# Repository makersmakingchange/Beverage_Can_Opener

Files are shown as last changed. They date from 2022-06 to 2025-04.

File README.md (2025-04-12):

# Beverage Can Opener
A tool to open beverage cans with a simple hook and lever motion.

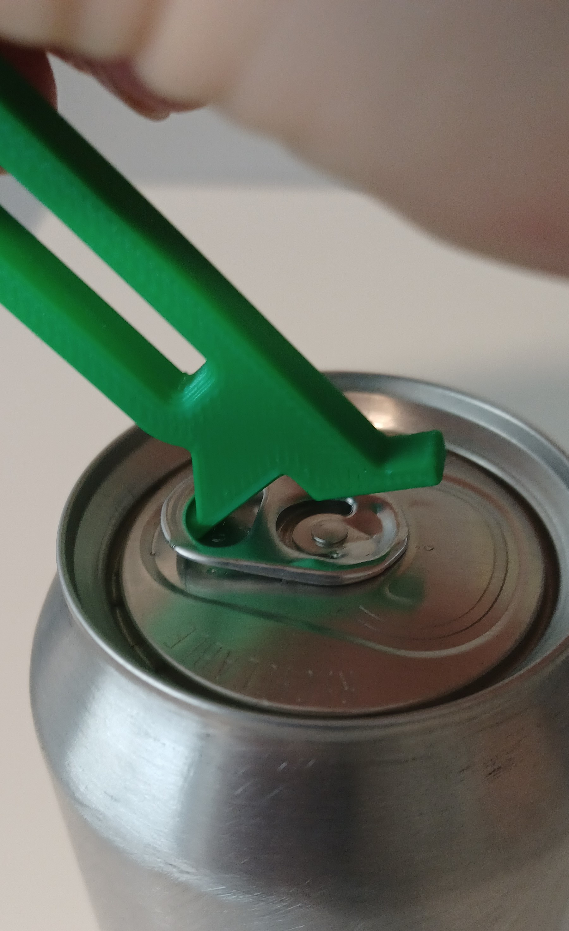
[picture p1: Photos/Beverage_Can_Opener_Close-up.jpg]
Picture of Printlab Can Opener.


## More info at
- [Makers Making Change Project Page](https://makersmakingchange.com/project/beverage-can-opener-from-printlab/)

## How to Obtain a Beverage Can Opener
### 1. Do it Yourself (DIY) or Do it Together (DIT)

This is an open-source assistive technology, so anyone is free to build it. All of the files and instructions required to build the Beverage Can Opener are contained within this repository. Refer to the Maker Checklist below.

### 2. Request a build of this device

If you would like to obtain a Beverage Can Opener, you may submit a build request through the [MMC Library Page](https://makersmakingchange.com/project/beverage-can-opener/). The requestor is responsible for the cost of materials and any shipping.

### 3. How to build this device for someone else

If you have the skills and equipment to build this device, and would like to donate your time to create the switch for someone who needs it, visit the [MMC Maker Wanted](https://makersmakingchange.com/maker-wanted/) section.

## Getting Started

### 1. Read the [Makers Checklist](/Documentation/Beverage_Can_Opener_Maker_Checklist_V1.0.pdf)

### 2. Print the Device

All of the print files can be in the [/Build_Files/3D_Print_Files](/Build_Files/3D_Print_Files/) folder.

Detailed instructions about 3D Printing settings can be found in the [3D Printing Guide](/Documentation/Beverage_Can_Opener_3D_Printing_Guide_V1.0.pdf).

## Files
### Documentation
| Document             | Version | Link |
|----------------------|---------|------|
| Design Rationale     | 1.0     | [Beverage_Can_Opener_Design_Rationale](/Documentation/Beverage_Can_Opener_Design_Rationale_V1.0.pdf)     |
| Maker Checklist      | 1.0     | [Beverage_Can_Opener_Maker_Checklist](/Documentation/Beverage_Can_Opener_Maker_Checklist_V1.0.pdf)     |
| Bill of Materials    | 1.0     | [Beverage_Can_Opener_Bill_of_Materials](/Documentation/Beverage_Can_Opener_BOM_V1.0.csv)     |
| 3D Printing Guide    | 1.0     | [Beverage_Can_Opener_3D_Printing_Guide](/Documentation/Beverage_Can_Opener_3D_Printing_Guide_V1.0.pdf)     |
| User Guide           | 1.0     | [Beverage_Can_Opener_User_Guide](/Documentation/Beverage_Can_Opener_User_Guide_V1.0.pdf)    |
| Changelog            | 1.0     | [Beverage_Can_Opener_Changelog](/Documentation/Beverage_Can_Opener_Changelog_V1.0.pdf)     |

### Design Files
[CAD Files](/Design_Files)

### Build Files
[3D Printing Files](/Build_Files/3D_Print_Files)

## Attribution
Original design by Jason Yeung.
Minor modifications to design and documentation by Neil Squire / Makers Making Change under the CC-BY-SA 4.0 License.
More information about Printlab can be found on their website: https://weareprintlab.com/  under the CC-BY-SA 4.0 License.

## License
Everything needed or used to design, make, test, or prepare the Beverage Can Opener is licensed under the CERN 2.0 Permissive license <https://ohwr.org/project/cernohl/wikis/Documents/CERN-OHL-version-2> (CERN-OHL-P) . 

<br /><span xmlns:dct="http://purl.org/dc/terms/" property="dct:title"><Device-Name></span> by <a xmlns:cc="http://creativecommons.org/ns#" href="www.makersmakingchange.com" property="cc:attributionName" rel="cc:attributionURL">Neil Squire</a> is licensed under a <a rel="license" href="http://creativecommons.org/licenses/by-sa/4.0/">Creative Commons Attribution-ShareAlike 4.0 International License</a>.

---
<!-- ABOUT MMC START -->
## About Makers Making Change
[Makers Making Change Logo](https://www.makersmakingchange.com/)

Makers Making Change is a program of [Neil Squire](https://www.neilsquire.ca/), a Canadian non-profit that uses technology, knowledge, and passion to empower people with disabilities.

Makers Making Change leverages the capacity of community based Makers, Disability Professionals and Volunteers to develop and deliver affordable Open Source Assistive Technologies.

 - Website: [www.MakersMakingChange.com](https://www.makersmakingchange.com/)
 - GitHub: [makersmakingchange](https://github.com/makersmakingchange)
 - Bluesky: [@makersmakingchange.bsky.social](https://bsky.app/profile/makersmakingchange.bsky.social)
 - Instagram: [@makersmakingchange](https://www.instagram.com/makersmakingchange)
 - Facebook: [makersmakechange](https://www.facebook.com/makersmakechange)
 - LinkedIn: [Neil Squire Society](https://www.linkedin.com/company/neil-squire-society/)
 - Thingiverse: [makersmakingchange](https://www.thingiverse.com/makersmakingchange/about)
 - Printables: [MakersMakingChange](https://www.printables.com/@MakersMakingChange)

### Contact Us
For technical questions, to get involved, or to share your experience we encourage you to [visit our website](https://www.makersmakingchange.com/) or [contact us](https://www.makersmakingchange.com/s/contact).
<!-- ABOUT MMC END -->

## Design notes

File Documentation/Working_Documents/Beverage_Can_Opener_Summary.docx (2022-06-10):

# Title

Beverage Can Opener.

## Subtitle

## A tool to open beverage cans with a simple hook and lever motion.

## Device Specifications

Build Time:

< 1hr

1-4 hr

5-10hr

>10hr

Cost:

$0 - $10

$11 - $25

$26 - $50

$51 - $100

$101 - $250

$250+

Stage: Recently Added

Skills: 3D Printing

Need: Agility / Dexterity

Disability: Mobility/Physical

Difficulty: Beginner

License: Attribution-ShareAlike 4.0 International

Usages: Aids for Daily Living (ADL), Mobility

Designer: Jason Yeung

## Device Details

### Overview

The Beverage Can Opener provides a way for those with arthritis, low finger dexterity, low vision, or other related disabilities to open beverage cans with a pull-tab with little strength or accuracy required.

This design is featured in the Assistive Device Academy from Printlab (https://classroom.weareprintlab.com/p/assistive-device-academy-v2).

### Compatibility

This device is compatible with aluminum beverage cans with pull-tabs.

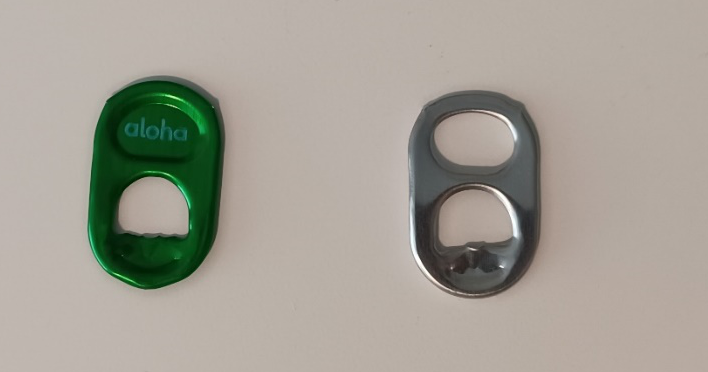
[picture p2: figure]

Some aluminum cans contain a pull-tab with some graphic or logo in the top hole of the tab, as seen in the left of the photo above. Only cans with a tab like the one shown on the right, with a hole in the top of the tab, can be used with this device.

### Similar Devices

- Another device for opening beverage cans, compatible with pull-tabs without a hole in the top (left in photo), is available at https://makersmakingchange.com/project/beverage-can-opener/ (https://makersmakingchange.com/?post_type=project&p=15048&preview=true).
- A device intended for tin food cans with pull-tabs, such as pet food, canned tuna or canned beans, is available at https://makersmakingchange.com/project/pull-tab-tin-can-opener/ (https://makersmakingchange.com/?post_type=project&p=15035&preview=true).

### Cost

Less than $1 CAD.

### Build Instructions

This device consists of a single 3D Printed Part. More comprehensive instructions on 3D Printing this device can be found in the Beverage Can Opener 3D Printing Guide.

#### Design

Full instructions for designing this device using CAD, along with other similar assistive devices, can be found in the Assistive Device Academy from Printlab (https://classroom.weareprintlab.com/p/assistive-device-academy-v2).

#### Skills Required

3D Printing.

#### Time Required

3D printing time: 38 minutes.

#### Tools

3D Printer

### Attribution

Original design by Jason Yeung.

Minor modifications to design and documentation by Neil Squire / Makers Making Change under the CC-BY-SA 4.0 License.

More information about Printlab can be found on their website: https://weareprintlab.com/ under the CC-BY-SA 4.0 License.

© 2022 by Neil Squire / Makers Making Change This work is licensed under the CC BY SA 4.0 License: http://creativecommons.org/licenses/by-sa/4.0 Files available at https://makersmakingchange.com/project/beverage-can-opener/ Page 1 of 2

V1.0 | June 2022 Beverage Can Opener Summary

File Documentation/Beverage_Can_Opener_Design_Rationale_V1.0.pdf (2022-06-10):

V1.0 | June 2022

## Beverage Can Opener

## DESIGN RATIONALE

© 2022 by Neil Squire / Makers Making Change This work is licensed under the CC BY SA 4.0 License: http://creativecommons.org/licenses/by-sa/4.0 Files available at https://makersmakingchange.com/project/beverage-can-opener/ (https://makersmakingchange.com/?post_type=project&p=15019&preview=true)

### Introduction

A device is needed in the Makers Making Change Assistive Device Library which can provide a way for those with arthritis, low finger dexterity, low vision, or other related disabilities open beverage cans with a pull-tab with little strength or accuracy needed.

This device is not intended for tin cans used for storing food, another device for that purpose is provided at https://makersmakingchange.com/project/pull-tab-tin-can-opener/. (https://makersmakingchange.com/?post_type=project&p=15035&preview=true)

### Requirements

### Goals

G01 | To provide a way for those with arthritis or low finger dexterity open the pull-tabs on beverage cans.
G02 | To provide a device cheaper than the commercial option.
G03 | To fit all pull-tabs on beverage cans available in grocery stores in Canada

### Functional Requirements

F01 Must not deteriorate with daily use.

### Non-functional Requirement

NF01 Must be 3D-printable in one piece with no supports.

### Constraints

C01 Must be cheaper than $5 to produce.

### Ideation

Since so many open-source designs are available for this device, it did not seem necessary to re-design a new product. Several different designs seemed promising using different methods to open the cans. The various designs and their pros and cons are listed below in the testing section.

One particular concern with some of the designs was the difference in the tabs of different beverage cans. Some tabs lack a hole in the top of the tabs which many can opener designs rely on.

## DESIGN RATIONALE

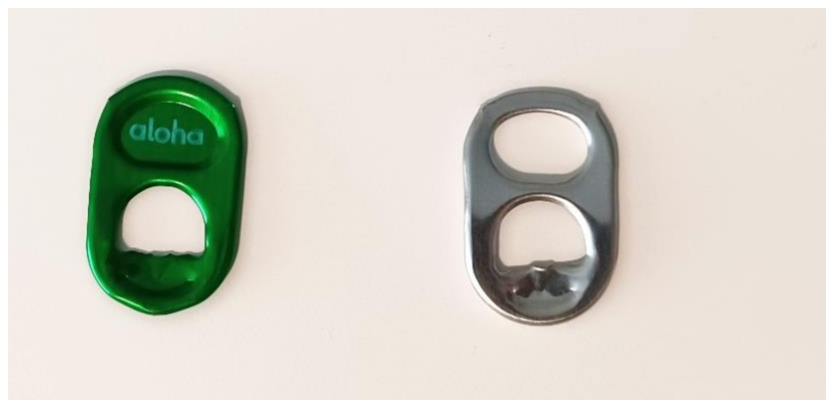
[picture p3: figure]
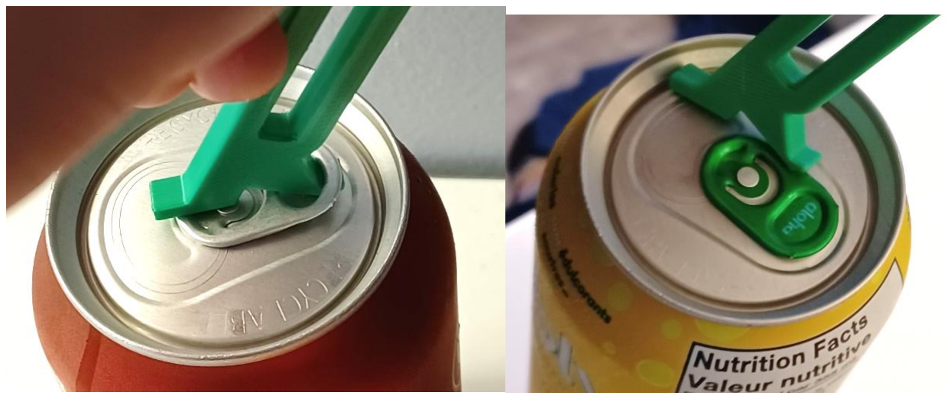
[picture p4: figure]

© 2022 by Neil Squire / Makers Making Change

Figure 1: An image showing the difference in Can Tabs. The bubly™ can tab lacks a hole which the generic pop can has. Other commercial drinks such as RedBull™ Energy drink lack this hole as well.

Figure 2: These 2 images demonstrate how a "hook-style" can opener cannot be used to open a beverage can without a tab which doesn't contain a hole in the top of the tab.

### Testing

A variety of open-source designs for can-openers were printed and tested for ease-of-use, ease-of-printing, and functionality.

## DESIGN RATIONALE

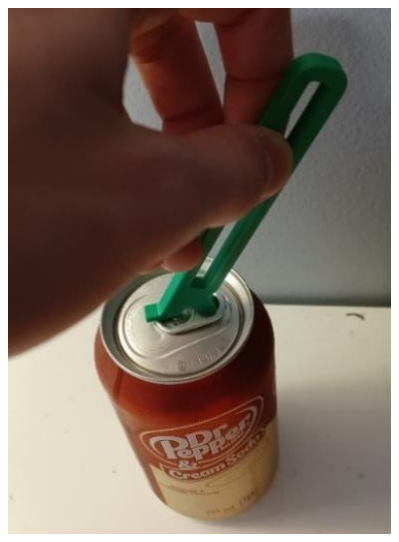
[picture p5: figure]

© 2022 by Neil Squire / Makers Making Change

Design 1: Jason from PrintLabs

Summary

This design uses a hook to grab the pull-tab using the top hole, then a levering action to open the can. The handle is large, easy to hold and the device is overall effective and easy to use.

Pros

- Easy and very quick to print (no support (~0.5 hours).
- Uses very little filament (~5 grams).
- Easy to use, large handle, lots of leverage.

Cons

- Does not work on bubly™ or energy drink pull-tabs.

## DESIGN RATIONALE

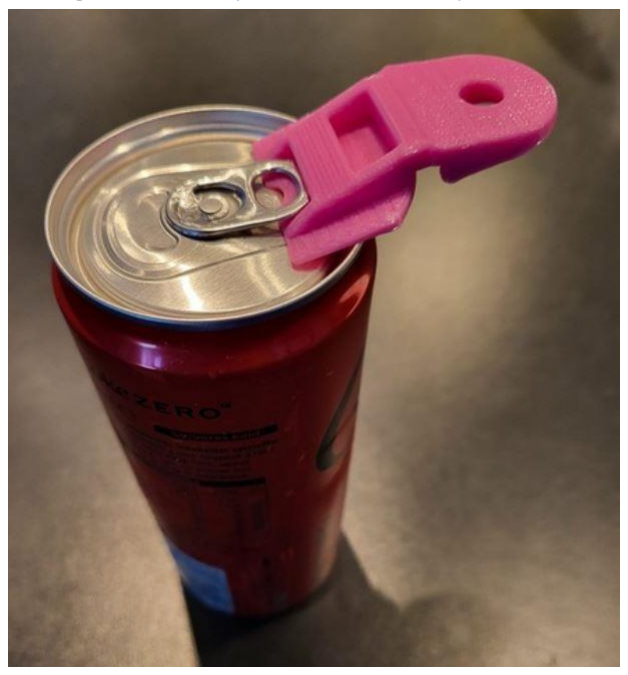
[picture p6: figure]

© 2022 by Neil Squire / Makers Making Change

Design 2: Can opener and lid by osund - Thingiverse (https://www.thingiverse.com/thing:5386671)

Summary

This is a small device which slides over the whole pull-tab of the can, allowing all tabs to be opened, including ones without a hole in the top. The small size of the device makes print time fast, and material use small. However, this comes at the expense of a difficult to hold and difficult to use device. This Can Opener also tends to slide off the tab while being used, making for a somewhat frustrating overall experience.

Pros

- Very easy and quick to print (no supports ~0.5 hours).
- Opens all styles of cans.
- Slides over pull-tab easily.
- Also serves as a lid to protect drink from flies once opened.

Cons

- Not very easy to use due to the device sliding off the pull-tab.
- Doesn’t give much leverage.

## DESIGN RATIONALE

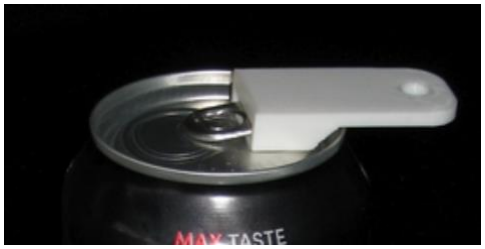
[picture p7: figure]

© 2022 by Neil Squire / Makers Making Change

Design 3: Pop Top Can Opener - Final by VegasGuy - Thingiverse (https://www.thingiverse.com/thing:3027499)

Summary

This device, like the one above, slides over the whole can pull-tab, allowing all tabs to be opened, including ones without a hole in the top. The Pop Top Can Opener is very small, making print time fast, material use small, but difficult to hold. However, this can opener is very effective, and for those with enough dexterity to hold the device, this Can Opener is probably the quickest and easiest to use on this list.

Pros

- Very easy and quick to print (no supports ~0.5 hours).
- Opens all styles of cans.
- Slides over pull-tab easily.
- Easy to use, effectively opens cans.

Cons

- Handle is tiny; can be difficult to hold.
- Design is closed for derivatives.

## DESIGN RATIONALE

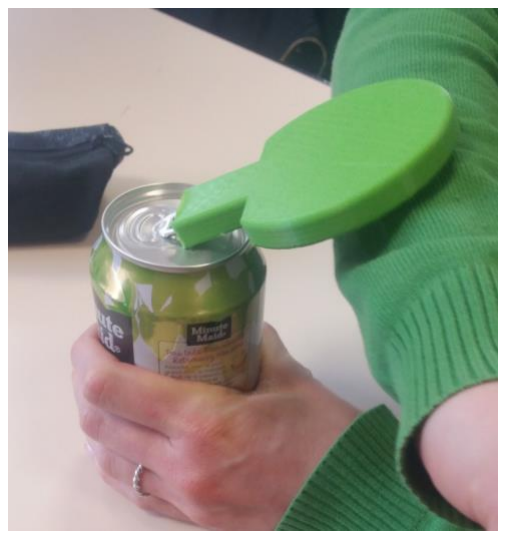
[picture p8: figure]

© 2022 by Neil Squire / Makers Making Change

Design 4: OT student project : Can opener helper by Pole_ergo - Thingiverse (https://www.thingiverse.com/thing:3846323)

Summary

The Can Opener Helper by Ergo Pole is different than other Can Openers in that it includes a huge, paddle-like surface for opening cans using an elbow or wrist. However, the design is flawed in that it doesn’t grip the can-tab well and easily slides off. This would be an easy modification however this design is closed for derivatives.

Pros

- Opens all styles of cans.
- Slides over pull-tab easily.
- Provides Larger Handle (Not sure how beneficial this is).

Cons

- Design is closed for derivatives.
- Longer Print time.
- Doesn’t open cans as effectively as expected (reversible design makes can opener slide off).

## DESIGN RATIONALE

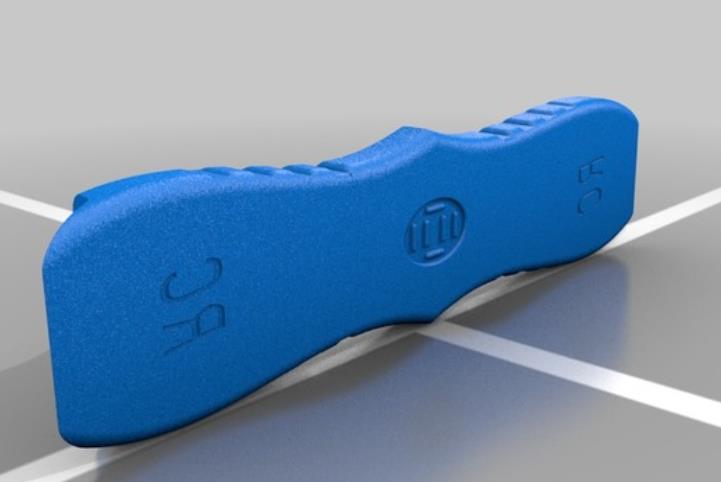
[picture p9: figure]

© 2022 by Neil Squire / Makers Making Change

Design 5: Soda Can Opener by ryancoretz - Thingiverse (https://www.thingiverse.com/thing:3697936)

Summary

This design also can also open pull-tabs with no hole in the top as it slides over the can pull-tabs. The handle is nice to hold in the hand, the device easily and snugly slides over the pull-tab, but this device most often fails to open cans, and instead bends the tab.

Pros

- Opens all styles of cans.
- Slides over pull-tab easily.
- Good size handle.
- Double-sided.

Cons

- Slightly longer print time (~1 hr).
- Will very often bend tab instead of opening can.
- Does not reliably open generic pop cans.

## DESIGN RATIONALE

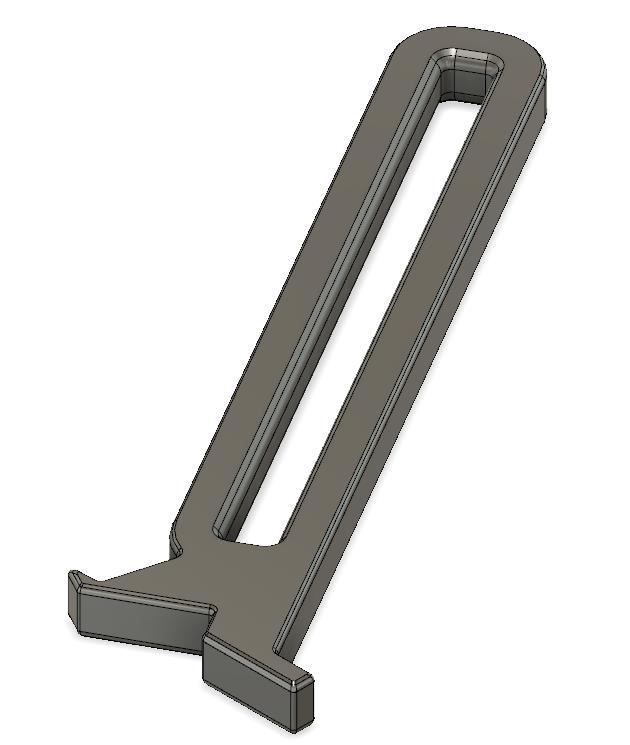
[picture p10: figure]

© 2022 by Neil Squire / Makers Making Change

### Detailed Design

Recommended design from testing: Design 1 - Jason from PrintLabs

The hook-style design from Jason at Printlab proved to be very quick to print, used very little filament, needed very little force to open the can and was easy to insert into the tab.

While this can opener cannot open the closed-hole style tabs, this device has many merits over other designs, so the Printlab Beverage Can Opener is beneficial to add to the Makers Making Change Device Library. A second can opener device will also be added for those who wish to open the closed-hole tabs.

The device is 106 mm long, 26 mm wide, and 6 mm thick.

### Opportunities for Improvement

- A design which can open beverage can tabs which have closed-hole style tab as well as the generic tabs may be beneficial to add to the library.

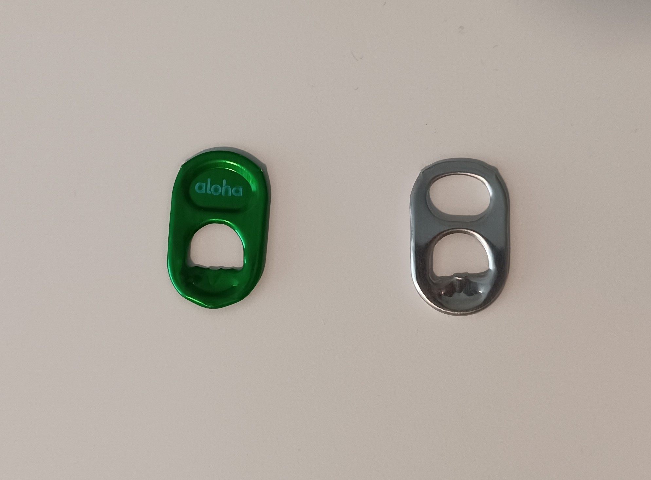
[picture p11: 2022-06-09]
Photos/Beverage_Can_Pull-Tab_Comparison.jpg

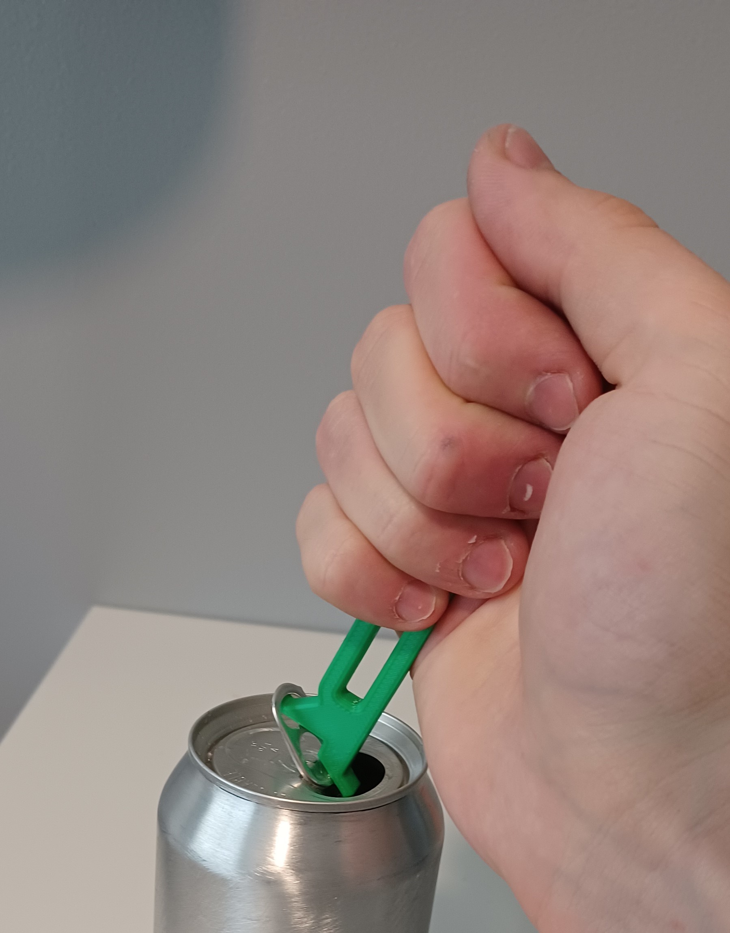
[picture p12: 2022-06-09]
Photos/Beverage_Can_Opener_Open_Can.jpg

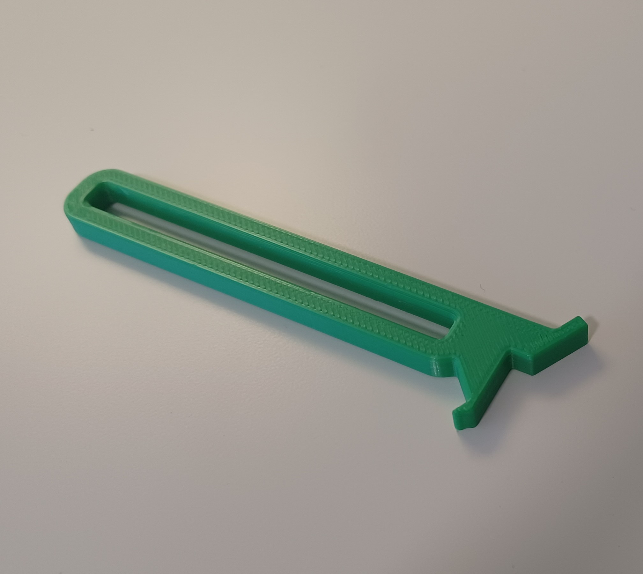
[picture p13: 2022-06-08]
Photos/Beverage_Can_Opener_Device_Only.jpg

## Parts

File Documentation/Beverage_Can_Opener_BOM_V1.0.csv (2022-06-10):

Device: Beverage Can Opener |  | Total Cost | Total Print time (hr) | Total filament (g)
Version: V1.0 | Date Created: 6/07/2022 | $0.13 | 0.63 | 5
3D Printed Parts ESTIMATED PRICING USING 1KG ROLL COST: | $25.00
Part | Description | Quantity Needed | TOTAL Mass (g) | Estimated Price | Print Time (Min) | Link
Beverage_Can_Opener.stl | The fully funtional Beverage Can Opener from Printlab, in a single piece. | 1 | 5 | $0.13 | 38 | https://github.com/makersmakingchange/Beverage_Can_Opener/tree/main/Build_Files/3D_Print_Files
 |  |  | Total Print Cost: | $0.13

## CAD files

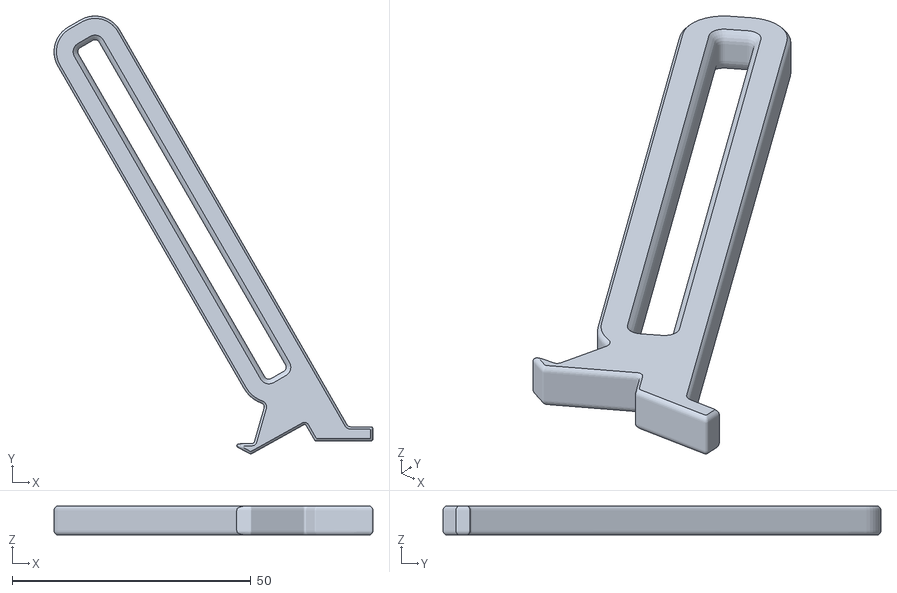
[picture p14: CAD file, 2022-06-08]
Build_Files/3D_Print_Files/Beverage_Can_Opener.stl
66.8 x 91.7 x 6.00

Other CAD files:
Design_Files/Beverage_Can_Opener.f3d

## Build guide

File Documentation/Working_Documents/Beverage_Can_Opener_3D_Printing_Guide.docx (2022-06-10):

# 3D Printing Summary

Metrics
Total Print Time (min) | 38
Total Number of Components | 1
Typical Total Mass (g) | 5
Typical Number of Print Setups | 1

# 3D Printing Settings

Print File Name | Qty | Total Print Time (hr:min) | Mass (g) | Infill (%) | Support | Layer Height/ Nozzle Diameter(mm) | Notes (orientation, special settings, etc.)
Beverage_Can_Opener.stl | 2 | 0:38 | 5 | 20 | No Support | 0.2/0.4 | - Must include at least 2 perimeters. - Ensure the print is oriented so that the flat side is laying on the print bed.

# Post-Processing

- Check for sharp edges and burrs. Remove as needed.

# Customization Options

- Can be printed in any colour

# Example of a Quality Print

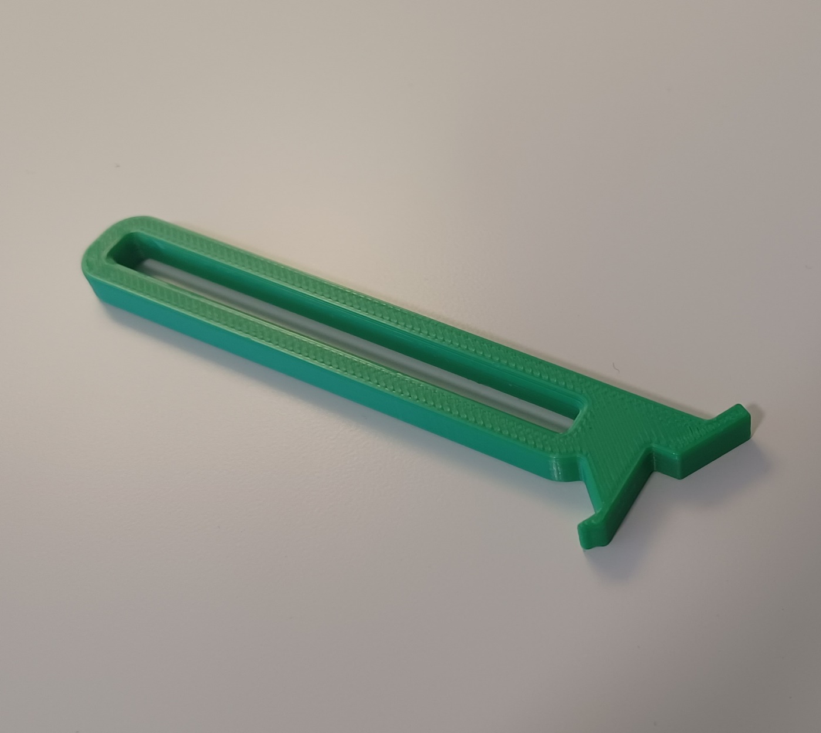
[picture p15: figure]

© 2022 by Neil Squire / Makers Making Change This work is licensed under the CC BY SA 4.0 License: http://creativecommons.org/licenses/by-sa/4.0 Files available at https://makersmakingchange.com/project/beverage-can-opener/ Page 1 of 2

V1.0 | June 2022 Beverage Can Opener 3D Printing Guide

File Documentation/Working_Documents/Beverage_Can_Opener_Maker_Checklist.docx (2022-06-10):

# Maker To Do List

- Read through the provided summary to familiarize yourself with the device and other available can opener options.
- Talk with user about the available options and determine which Can Opener is best suited to their needs.
- 3D Print Device.
- Test device.
- Print User Guide.

# Items to Give to User

- Printed, tested device.
- User Guide.

© 2022 by Neil Squire / Makers Making Change This work is licensed under the CC BY SA 4.0 License: http://creativecommons.org/licenses/by-sa/4.0 Files available at https://makersmakingchange.com/project/beverage-can-opener/ Page 1 of 1

V1.0 | June 2022 Beverage Can Opener Maker Checklist

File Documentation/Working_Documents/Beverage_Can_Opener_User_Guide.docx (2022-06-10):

## Introduction

This device is used to open the pull-tabs of beverage cans by simply placing the hook inside the top loop of the can pull-tab and using a lever motion.

## Features

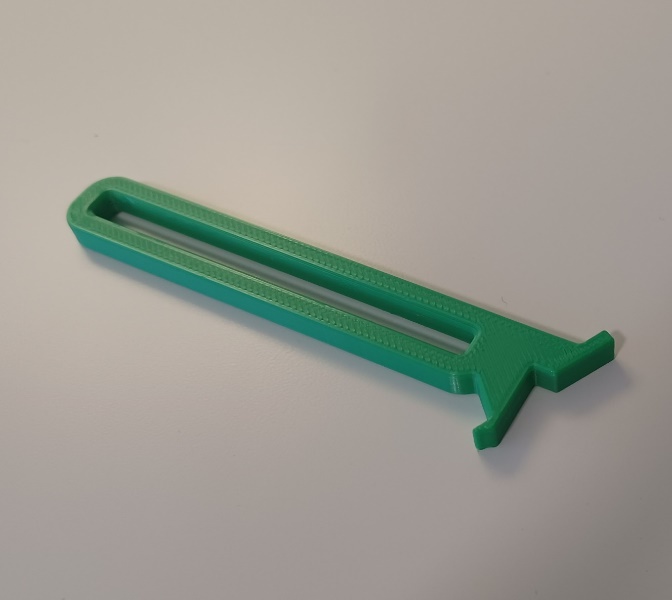
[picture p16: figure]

Handle

Hook for Can Pull-Tab

## Compatibility

This device is compatible with aluminum beverage cans with pull tabs.

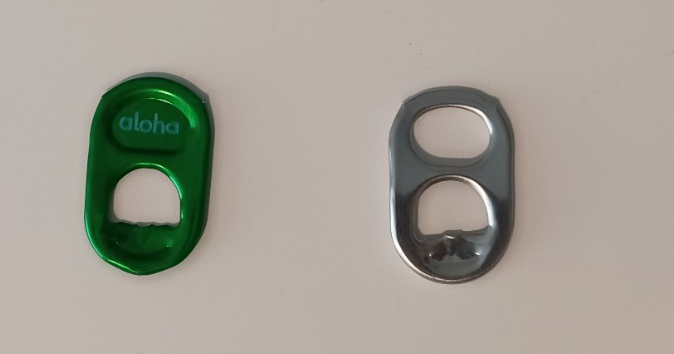
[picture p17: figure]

Some aluminum cans contain a pull-tab with some graphic or logo in the top hole of the tab, as seen in the left of the photo above. Only cans with a tab like the one shown on the right, with a hole in the top of the tab, can be used with this device.

## Usage

1. Slide the hook of the Can Opener into the hole in the top of the can pull-tab.

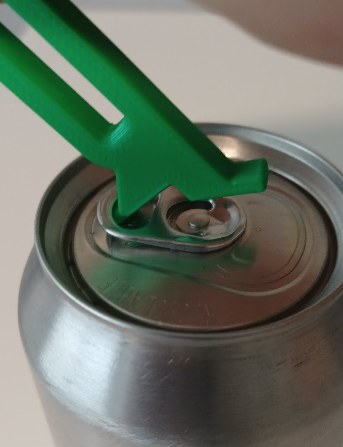
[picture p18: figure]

2. Grip the Can opener and pull backwards like pulling a lever.

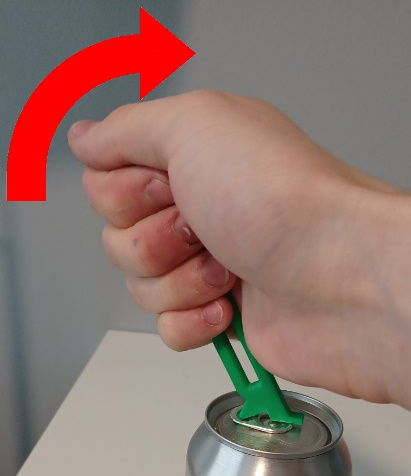
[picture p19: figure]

## Specifications

The device should be approximately 106 mm long, 26 mm wide, and 6 mm thick.

## Cleaning

Wipe with sterilizing cloth or spray with sterilizing spray. Do not expose to high heat or wash in dishwasher.

© 2022 by Neil Squire / Makers Making Change This work is licensed under the CC BY SA 4.0 License: http://creativecommons.org/licenses/by-sa/4.0 Files available at https://makersmakingchange.com/project/beverage-can-opener/ Page 2 of 3

V1.0 | June 2022 Beverage Can Opener user Quick Guide

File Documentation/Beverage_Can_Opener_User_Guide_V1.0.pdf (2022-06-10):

V1.0 | June 2022

## Beverage Can Opener

## USER QUICK GUIDE

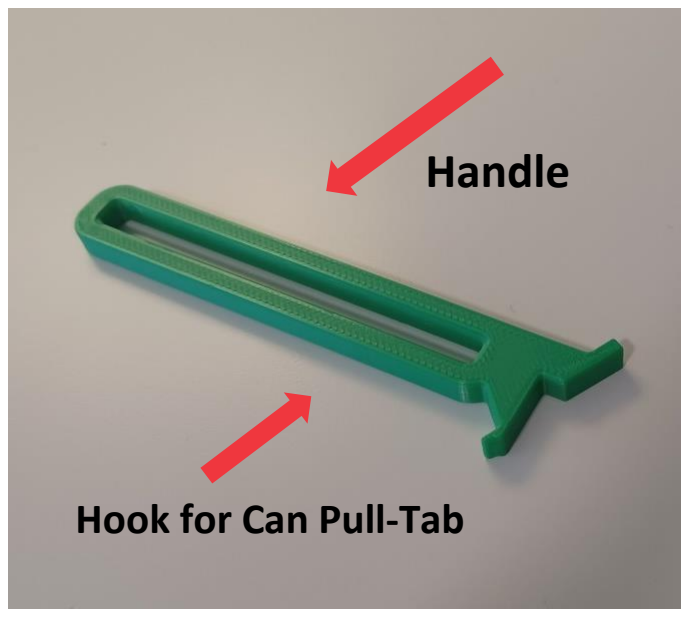
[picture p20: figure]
Handle; Hook for Can Pull-Tab
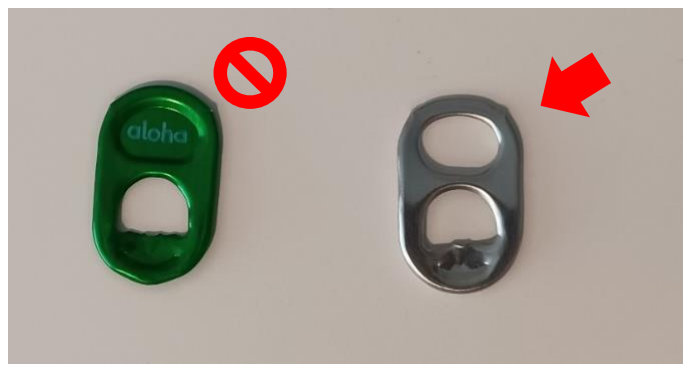
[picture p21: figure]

© 2022 by Neil Squire (https://neilsquire.ca/) / Makers Making Change

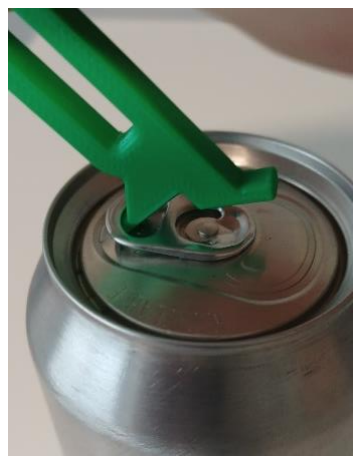
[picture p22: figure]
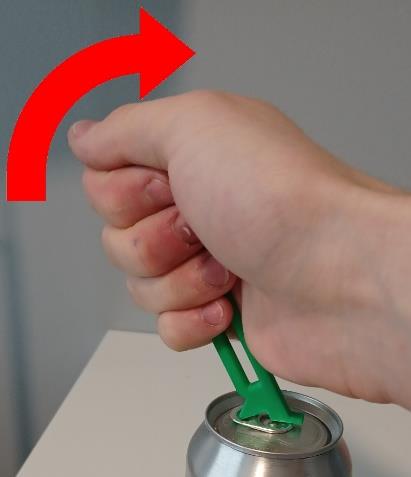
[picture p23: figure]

This work is licensed under the CC BY SA 4.0 License: http://creativecommons.org/licenses/by-sa/4.0 Files available at https://makersmakingchange.com/project/beverage-can-opener/ (https://makersmakingchange.com/?post_type=project&p=15019&preview=true)

### Introduction

This device is used to open the pull-tabs of beverage cans by simply placing the hook inside the top loop of the can pull-tab and using a lever motion.

### Features

### Compatibility

This device is compatible with aluminum beverage cans with pull tabs.

Some aluminum cans contain a pull-tab with some graphic or logo in the top hole of the tab, as seen in the left of the photo above. Only cans with a tab like the one shown on the right, with a hole in the top of the tab, can be used with this device.

### Usage

1. Slide the hook of the Can Opener into the hole in the top of the can pull-tab.
2. Grip the Can opener and pull backwards like pulling a lever.

### Specifications

The device should be approximately 106 mm long, 26 mm wide, and 6 mm thick.

### Cleaning

Wipe with sterilizing cloth or spray with sterilizing spray. Do not expose to high heat or wash in dishwasher.

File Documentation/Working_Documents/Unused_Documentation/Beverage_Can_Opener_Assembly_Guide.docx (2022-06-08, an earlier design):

# Required Components

<Insert a photo with all components of the device laid out and labelled with number that correspond to the numbers in the cell to the right. Add appropriate Alt text> | BOM

# Required Tools

# Required Personal Protective Equipment (PPE)

# Assembly Instructions

## Step 1

<Description>

<Insert photo here. Make sure to add appropriate alt text>

## Step 2

<Description>

<Insert photo here. Make sure to add appropriate alt text >

## Step 3

<Description>

<Insert photo here. Make sure to add appropriate alt text >

<Add additional steps as necessary

© 2022 by <Author>. This work is licensed under the CC BY SA 4.0 License: http://creativecommons.org/licenses/by-sa/4.0 Files available at <Replace with MMC Library Link> Page 1 of 1

VX.X | <MONTH> <YEAR> <Device Name> Assembly Guide

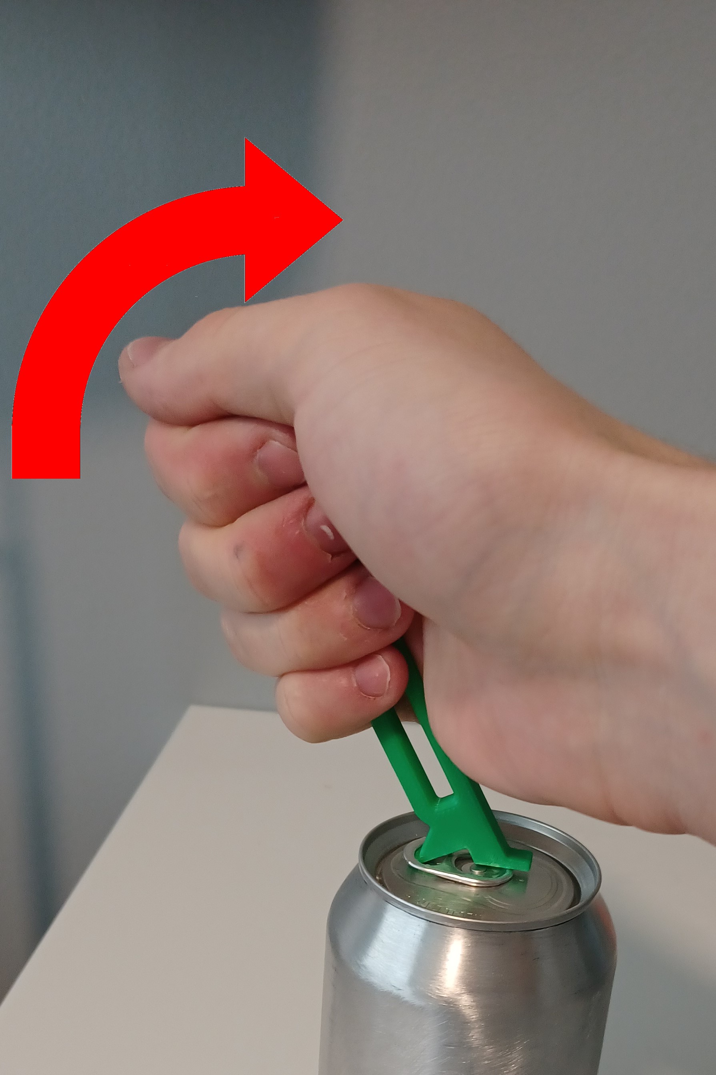
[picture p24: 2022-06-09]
Photos/Beverage_Can_Opener_Opening_Guide.jpg

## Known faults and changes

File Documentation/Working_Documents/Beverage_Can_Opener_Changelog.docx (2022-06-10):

# Version 1.0 | Date 06/07/2022

- New design added to library created by Jason Yeung from Printlab.
- Fillets and chamfers added according to Design Rules for FFF 3D Printing - Hydra Research (https://www.hydraresearch3d.com/design-rules) to ensure comfort in user’s hand.

© 2022 by Neil Squire / Makers Making Change This work is licensed under the CC BY SA 4.0 License: http://creativecommons.org/licenses/by-sa/4.0 Files available at https://makersmakingchange.com/project/beverage-can-opener/ Page 1 of 1

V1.0 | June 2022 Beverage Can Opener changelog

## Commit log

2022-06-08 Added GitHub link to BOM
    [Printlab_Beverage_Can_Opener_BOM.xlsx, Printlab_Beverage_Can_Opener_BOM_V1.0.csv]
2022-06-10 Rename Project
    Rename of Project from Printlab Beverage Can Opener to Beverage Can Opener
    [Beverage_Can_Opener.f3d, Beverage_Can_Opener.stl, Beverage_Can_Opener_BOM.xlsx, Beverage_Can_Opener_BOM_V1.0.csv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]
2022-06-10 Fixed BOM and 3D Printing Guide
    [Beverage_Can_Opener_BOM.xlsx, Beverage_Can_Opener_BOM_V1.0.csv]
